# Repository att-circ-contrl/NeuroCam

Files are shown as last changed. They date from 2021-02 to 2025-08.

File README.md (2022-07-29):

# NeuroCam Experiment Monitoring System

## Overview

The NeuroCam is a set of scripts designed to aggregate video footage from
multiple cameras and to let a user monitor and annotate that footage in
real-time. Frame alignment is performed in post-processing, and video footage
is saved frame-by-frame to allow later analysis without motion-compression
artifacts.

**While this code is functional, there is a lot of room for improvement.**
This is documented in more detail in the "Idiosyncracies" section of this
document and in the "TODO" documentation in the code folder. Most of these
improvements will eventually happen, but refactoring NeuroCam is not
presently the lab's top priority.

The NeuroCam project is copyright (c) by Vanderbilt University, and is
released under the Creative Commons Attribution-ShareAlike 4.0 International
License.

## Quick-Start

The top-level Makefile automates common operations (under Ubuntu-derived
Linux, at least):

* Type "`make`" without arguments for the Makefile target list.

* To make a NeuroCam software install/update USB stick, put a USB stick in
your machine and type "`make installkey`".

* To rebuild the manuals (which should already be in the "`manuals`" folder),
type "`make manual`".

* To flash a "Blink Box" GPIO device using the firmware hex file, plug the
device into your computer and type "`make blinkbox-burn`".

* To rebuild the firmware for the "Blink Box" GPIO device, make sure
the "NeurAVR" project is installed and "`neuravr`" is symlinked at an
appropriate location (in the "`gpio/code`" folder or in the folder the
"`NeuroCam`" project is installed in), and type "`make blinkbox-hex`".

## Relevant Components

The following hardware and software components are provided:

* **Control daemon script.** This listens for commands on a UDP port, starts
and stops the camera daemon and GPIO daemon, and performs post-processing
tasks as requested.

* **Web interface script.** This is an old-school CGI script that provides a
GUI for configuring, controlling, and monitoring the output of the NeuroCam
control daemon.

* **Command-line interface program.** This is a command-line script that
can configure and command the NeuroCam control daemon.

* **"Blink Box" GPIO device.** This is a general-purpose TTL I/O box built
using Arduino hardware. The NeuroCam uses it to strobe LEDs for frame
synchronization and to listen for TTL signals (start/stop strobes and
annotation signals).

* **GPIO monitoring daemon.** This probes for "Blink Box" GPIO devices, and
if found, sets up LED strobing and translates GPIO inputs into appropriate
UDP commands that are sent to the NeuroCam control daemon.

The following helper scripts are provided:

* **Install and update scripts.** These are used to create NeuroCam software
installation USB sticks, which are then used to make new NeuroCams and to
update their software.

* **Utility scripts.** At present, this is a pair of scripts for sending UDP
packets and listening for UDP broadcasts. These are used for low-level
communication with the NeuroCam daemon for debugging purposes.

## Idiosyncracies

The following idiosyncracies are present (per "there is a lot of room for
improvement" in the overview section):

* Frame-grabbing has low jitter once it's been started but the individual
streams have time skew of up to 0.25 seconds relative to each other. This
is probably due to startup time of the frame-grabbing tool used (invoked via
shell call).

The workaround is to use LED strobing for frame alignment in post-processing.

* Compositing for monitoring and during post-processing takes far longer
than it should. This is probably due to using the Perl ImageMagick libraries
rather than writing a C utility using libjpeg to do it.

The workaround is to throw hardware at the problem (at least one core per
camera).

* Between capture time skew and compositing delay, there's about half a
second of time lag on the monitoring stream that the user sees. The frame
rate of the monitoring stream is also lower than the actual capture frame
rate (as the compositing process will drop frames as-needed; the frames
themselves are still saved).

The workaround is to click on a given individual feed in the web GUI to
select a specific raw feed, which is then forwarded without compositing,
if faster access is needed.

* The NeuroCam does not have a proper job manager (i.e. it isn't possible
to queue multiple operations). This is high on the list of features to
implement, but NeuroCam development is not presently the lab's top priority.

The workaround is to babysit the NeuroCam during post-processing and file
transfer. Folders (capture sessions) have to be processed, moved, or
deleted individually.

* The NeuroCam generates an absurdly large number of files (one per frame
per camera), and stores each camera's frames in a single directory.

This is intentional, but _many_ filesystems really hate having directories
with large numbers of files in them. In particular, the `exfat` filesystem
used on most external drives slows to a crawl, and the default Windows and
MacOS filesystems don't like it either. The default Linux filesystems
(`ext2`/`ext3`/`ext4`) are okay with it.

The workaround is to store NeuroCam folders as `.tar` archives when saving
them on external drives, and to process the frame data on Linux machines or
on other machines with suitable filesystems configured.

* The NeuroCam performs random access to an absurdly large number of files
during capture and post-processing.

This is intentional, and is unavoidable for data saved as individual frames.
It means that solid-state drives should be used when building NeuroCam
systems, as the seek time of magnetic drives would slow processing to a
crawl (and probably capture, too).

## Folders

This repository contains the following directories:

* `code` -- NeuroCam daemon and GUI scripts.
* `drawings` - Mechanical drawings (for the GPIO device).
* `gpio` -- Firmware source and PCB development files for the "Blink Box"
GPIO device.
* `hexfiles` -- Firmware binaries for the "Blink Box" GPIO device.
* `install-scripts` -- Scripts for building install/update USB sticks.
* `manuals` -- NeuroCam documentation.
* `manuals-src` -- Source for rebuilding NeuroCam documentation.
* `matlab` -- Matlab libraries for working with NeuroCam systems and data.
* `notes` -- Miscellaneous notes relevant to NeuroCam development.
* `schematics` - Schematics (for the GPIO device and lamp driver).
* `utils` -- Miscellaneous utility scripts for debugging the NeuroCam.

_This is the end of the file._

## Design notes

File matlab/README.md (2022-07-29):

# NeuroCam Experiment Monitoring System - Matlab Libraries

## Overview

This is a set of Matlab libraries and test scripts written to support the
use of the NeuroCam system.

These files are part of the NeuroCam project.
This project is Copyright (c) 2021 by Vanderbilt University, and is released
under the Creative Commons Attribution-ShareAlike 4.0 International License.

## Libraries

* `lib-ncam-video` --
Library for reading video frame information from a repository and for
extracting information about rapid brightness changes, to use for time
alignment.

## Sample Code

Sample code scripts are intended to illustrate how the libraries are used.
These also include my development test scripts. The following scripts are
provided:

* `do_align.m` --
Performs video frame alignment on a dataset using brightness changes in the
images (rather than LED blinks). This is intended to catch situations where
a computer monitor in view changes its depicted scene (a large change in
brightness in a one-frame time step). This should catch LED blinks too.

_This is the end of the file._

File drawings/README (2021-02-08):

EPS can be converted to DXF by loading into and saving from Inkscape.
This messes with the scale factor. I think it did 1 pt = 1 mm.

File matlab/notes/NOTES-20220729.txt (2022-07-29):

This is an interim partial version of the alignment script that makes
histograms of difference data but doesn't do anything else with it.

As far as I can tell by eye, the best way to proceed is to look for the most
variable sqrt(n) tiles in any given stream and average those, rather than
looking at the full-frame average.

It may also be a good idea to get a correlation matrix between tiles and
group tile sets that are most correlated, within a stream. This would catch
the case where two areas of the image are highly variable but are behaving
very differently.

Alternatively we could just select the top sqrt(n) tiles individually without
averaging them, and use each of them as alignment candidates against other
streams' tiles.

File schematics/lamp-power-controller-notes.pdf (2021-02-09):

Christopher Thomas <christopher.thomas.webmail@gmail.com>

## Lamp control circuit

2 messages

Christopher Thomas <christopher.thomas.webmail@gmail.com> | Wed, Nov 27, 2019 at 11:46 AM
To: "Haniff, Isaac J" <isaac.j.haniff@vanderbilt.edu>

Here are cleaned-up schematics and layout drawings for the lamp control circuit. It'll work as a general purpose "let a TTL line control a power supply" widget, so I figured you might eventually find it useful elsewhere.

My rating limits (24V 0.8A) are conservative. The actual limits are probably about 30V and 1.5A. The parts' absolute limits are 40V and 2A, but going anywhere near those is a bad and fire-prone idea.

The FETs are BS170 TO-92 ones (very common). The resistors should be at least 10k but other than that can be anything. The tiny 1" breadboard I used is Digikey part number 1568-1652-ND or SparkFun part number PRT-08808. The tiny box I used is Digikey part number HM-375-ND. The BNC pigtail was Digikey part number 314-1190-ND (handy to stock for many projects, but pricy). If you're screwing the board down rather than leaving it free-hanging, you'll want a 1/8" #4 stand-off, a #4-40 screw (1/2" or 5/8"), and a #4-40 hex nut as well.

I hope that you find this useful!

Regards,
-Christopher Thomas

### 2 attachments

lamp-control-schem.png
36K

lamp-control-bread-layout.png 133K

Christopher Thomas <christopher.thomas.webmail@gmail.com> | Wed, Nov 27, 2019 at 11:59 AM
To: "Haniff, Isaac J" <isaac.j.haniff@vanderbilt.edu>

In case you're wondering about some of the resistors: The BS170's maximum gate voltage is 20V. The resistors divide down the pull-up voltage, to tolerate a maximum of 40V. If you made the top resistors 20k and kept the others at 10k, you could tolerate up to 60V in, which is the same as the BS170's maximum drain-to-source voltage. This would only be a good idea if you knew the supply voltage was going to be high, though, as you want the gate voltage to be about 10V or higher to get decent current output.

For power calculations, the worst-case output resistance per transistor is 5 ohms, and absolute maximum power is 0.8W. That gives an absolute maximum current of 0.4A per transistor (at the worst-case resistance). If you've ever touched a 1W resistor with bare fingers, you'll understand why I added headroom. Junction-to-ambient thermal resistance is 150 degC/W, giving a 30 degC rise at my de-rated value (or 120 degC at their maximum; water boils at 100 degC).

Long story short, you can scale up output current by adding more FETs in parallel. FETS, unlike bipolars, have a negative temperature coefficient and so don't suffer from current hogging or thermal runaway. For much larger than this, you'd probably instead use a TO-220 FET bolted to a heat sink as the output driver.

Regards,
-Christopher Thomas
Gmail - Lamp control circuit | https://mail.google.com/mail/u/0?ik=50e6ba25c9...
1 of 1 | 2019-11-27, 12:01 p.m.

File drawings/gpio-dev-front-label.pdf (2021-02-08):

7 0

## Gnd GPIO TTL

Visible LEDs IR LED

7 0

## Gnd GPIO TTL

7 0

## Gnd GPIO TTL

Visible LEDs IR LED

7 0

Gnd

Visible LEDs

## GPIO TTL

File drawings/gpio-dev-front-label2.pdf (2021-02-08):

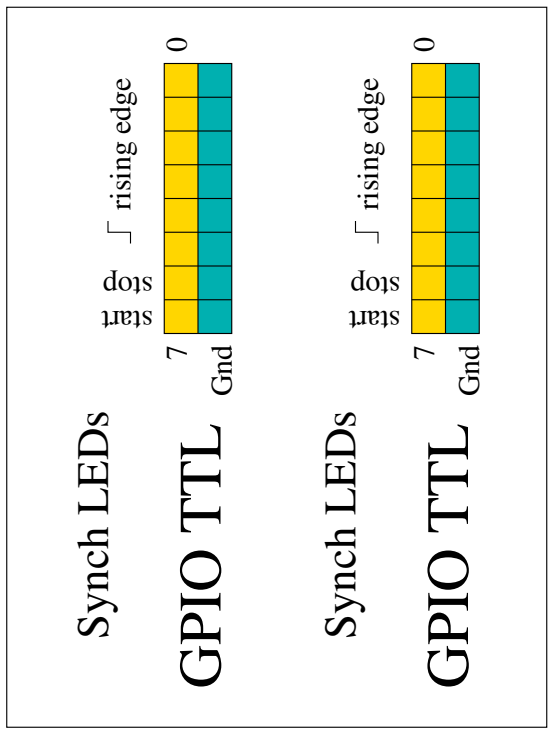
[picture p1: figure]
Gnd GPIO TTL; Synch LEDs

Gnd GPIO TTL; Synch LEDs

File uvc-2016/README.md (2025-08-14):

# UVC Driver Notes

The 2016 version of the NeuroCam (running on Mint 17) had an issue where
certain cameras would attempt to grab all of the available USB bandwidth.
This folder contains the diff made to "`uvc_video.c`" to address that issue,
along with additional notes.

For further details, see `notes/NOTES-uvc`.

Systems based on later versions of Mint did not appear to have this issue.

_This is the end of the file._

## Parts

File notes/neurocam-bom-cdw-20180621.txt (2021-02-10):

Machine (no RAM):  NUC6i7KYK  CDW p/n: 4085713   (545.99 USD)
RAM:  Kingston DDR4 2x4gig  CDW p/n: 4039935   (114.99 USD)
SSD:  (1 TB) Samsung MZ-N5E1T0BW  CDW p/n: 4150865   (418.99 USD)
(3x) Camera:  Logitech C920  CDW p/n: 2588857   (72.99 USD)
USB hub:  StarTech 4-port  CDW p/n: 3069185   (25.99 USD)
Router:  Asus N16  CDW p/n: 1953395  (93.99 USD)
[alternate: Asus RT-N66R  CDW p/n:  4493141  (93.99 USD)]
Patch cable:  Tripp Lite 3' Cat5e  CDW p/n: 324473  (2.99 USD)

Unit cost:  1422 USD (approx)

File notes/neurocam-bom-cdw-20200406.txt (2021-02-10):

Part			mfg p/n		cdw p/n		price

machine (no RAM)	NUC7i7DNKE	5008529		659.99
https://www.cdw.com/product/intel-next-unit-of-computing-kit-nuc7i7dnke-mini-pc-core-i7-8650u-1.9-g/5008529

RAM (1x8 gigs)		KCP426SS8/8	5109912		43.99
https://www.cdw.com/product/kingston-ddr4-8-gb-so-dimm-260-pin-unbuffered/5109912

SSD (1 TB)		MZ-N6E1T0BW	4934196		183.99
https://www.cdw.com/product/samsung-860-evo-mz-n6e1t0bw-solid-state-drive-1-tb-sata-6gb-s/4934196

Router			RT-N66R		4493141		99.99
https://www.cdw.com/product/asus-rt-n66r-wireless-router-802.11a-b-g-n-desktop/4493141

USB hub (usb 3)		ST4300MINU3B	3069185		25.99
https://www.cdw.com/product/startech.com-portable-4-port-superspeed-mini-usb-3.0-hub-black/3069185

Network cable (3')	N001-003-BL	324473		2.99
https://www.cdw.com/product/tripp-lite-3ft-cat5e-cat5-350mhz-blue-snagless-molded-patch-cable-rj45-m-m/324473

Total:							1016.94

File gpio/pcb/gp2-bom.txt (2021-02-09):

Gp2 Uno shield rc1 bill of materials (USD):

Item                    Digikey p/n        Unit Price    Qty      Cost

header male 1x6         732-5319-ND         0.33          1        0.33
header male 1x8         732-5321-ND         0.37          2        0.74
header male 1x10        732-2670-ND         0.89          1        0.89
header female 2x3       S7071-ND            0.61          1        0.61
header male 2x6 shr     SAM12292-ND         2.80          1        2.80
header male 2x8 shr     S9171-ND            0.42          1        0.42

resistor 0805 680 ohm   P680CCT-ND          0.11          1        0.11
resistor 0805 47 kohm   P47.0KCCT-ND        0.11          1        0.11
resistor 0805 475 kohm  P475KCCT-ND         0.10         12        1.20

Subtotal:                                                          7.21

Gp2 faceplate rc3 bill of materials (USD):

Item                    Digikey p/n        Unit Price    Qty      Cost

header male 2x6 shr     SAM12292-ND         2.80          1        2.80
header male 2x8 shr     S9171-ND            0.42          1        0.42

BNC jack (pcb) 50 ohm   WM5278-ND           4.03          8       32.24
LED green 3mm           4303F5-ND           0.61          1        0.61
LED red 3mm             4303F1-ND           0.59          1        0.59
switch pb SPST          SW1021CT-ND         1.00          1        1.00

transistor nfet to-92   BS170-ND            0.56          8        4.48

resistor 0805 680 ohm   P680CCT-ND          0.11          8        0.88
resistor 0805 47 kohm   P47.0KCCT-ND        0.11          1        0.11

Subtotal:                                                         43.13

Auxiliary hardware (USD):

Item                    Digikey p/n        Unit Price    Qty      Cost

Arduino Uno rev3        1050-1024-ND       23.38          1       23.38

(no such thing as a 12-position pre-assembled cable.)
ribbon cable 12pos 1m   732-11802-ND        2.55          1        2.55
IDC connector 12pos     A113153-ND          1.88          2        3.76

box metal/abs 6.3"x6.5" HM904-ND           21.45          1       21.45

USB B panel mount       1528-1570-ND        3.95          1        3.95
USB A-B cable 3'        1175-1087-ND        2.48          1        2.48

spacer nylon 4-40 3/4"  36-1902D-ND         0.90          4        3.60
spacer nylon #4 1/16"   492-1071-ND         0.0520        6        0.31
screw nylon 4-40 3/4"   H550-ND             0.0926        4        0.37
screw nylon 4-40 1/4"   H542-ND             0.0886        4        0.35
screw metal 4-40 3/8"   HM1456-ND           0.109         6        0.65
hex nut nylon 4-40      36-9605-ND          0.161        10        1.61

Subtotal:                                                         64.46

Printed circuit boards (USD):
(via Seeed Studio, in quantity 10)

Item                                       Unit Price    Qty      Cost

front panel PCB                             1.832         1        1.83
shield PCB                                  0.49          1        0.49

Subtotal:                                                          2.32

Grand total:                                                     117.12

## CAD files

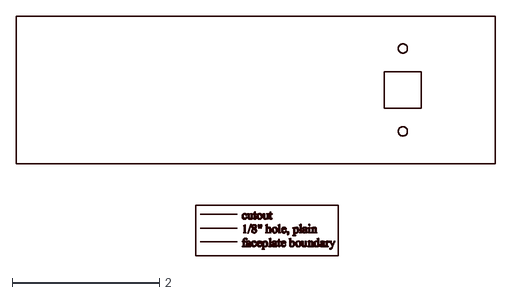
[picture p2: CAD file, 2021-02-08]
drawings/gpio-v2-back-inches.dxf
6.50 x 3.25

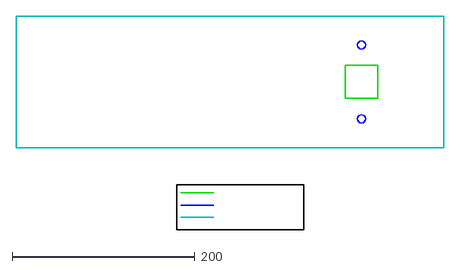
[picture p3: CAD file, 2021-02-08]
drawings/gpio-v2-back.dxf
468.0 x 234.0

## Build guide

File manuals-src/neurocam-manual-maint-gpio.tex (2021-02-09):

% NeuroCam manual - GPIO/Synch Boxes
% Written by Christopher Thomas.
% Copyright (c) 2021 by Vanderbilt University. This work is released under
% the Creative Commons Attribution-ShareAlike 4.0 International License.

\chapter{GPIO and Synch Box}
\label{gpio}

The GPIO-and-synch box provides TTL-level inputs via a rectangular connector
and TTL-level synchronization outputs via BNC connectors. Changes to inputs
are reported to the NeuroCam computer via USB cable.

During normal operation of the NeuroCam system, the following functions are
performed:
\begin{itemize}
\item The synchronization lines are strobed high for 20~ms every 10 seconds,
with changes in the outputs recorded in session log files.
\item Changes to TTL inputs are recorded in session log files.
\item Low-to-high transitions on input bits 7 and 6 cause the NeuroCam to
start and stop recording a session, respectively. There is a ``dead time''
of 10 seconds between successive commands being recognized.
\end{itemize}

The front panel and interior of a GPIO-and-synch box are shown below:

\begin{center}
% The exterior image is 800x600, the interior is 600x600.
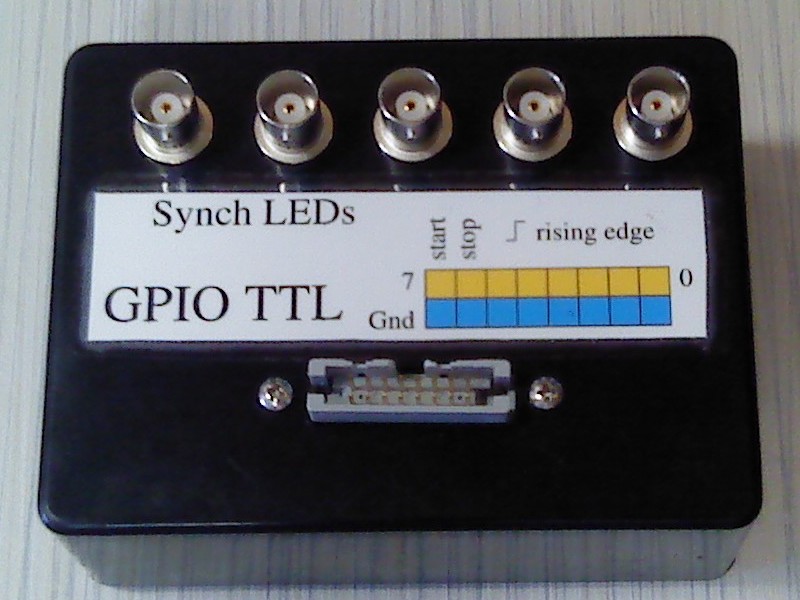
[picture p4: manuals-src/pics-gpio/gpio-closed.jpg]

\hspace{1in}
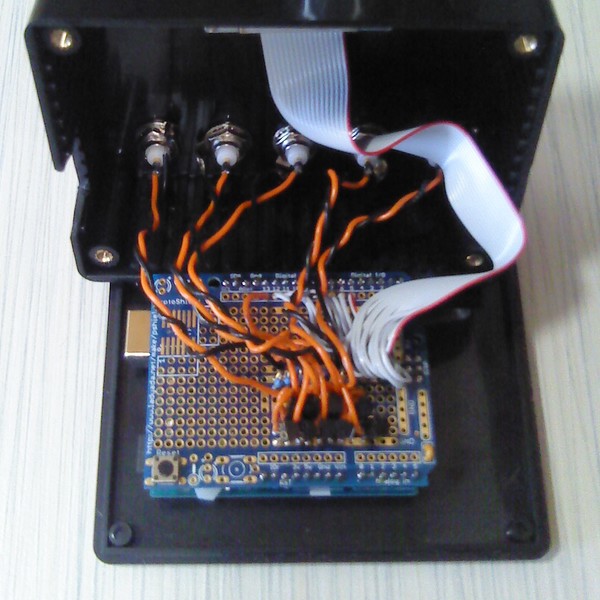
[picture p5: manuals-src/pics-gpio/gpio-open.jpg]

\end{center}

\clearpage
The parts needed for a GPIO-and-synch box are as follows:

\begin{tabular}{llll}\hline
Qty & Description & Manuf. p/n & Digikey p/n \\
\hline
%
1 & Arduino Uno rev3 & A000066 & 1050-1024-ND \\
1 & Arduino prototyping shield kit & 2077 & 1528-1207-ND \\
9 & NFET TO-92 & BS170 & BS170-ND \\
3 & resistor 4.75 kohm 0.25w & MFR-25FBF52-4K75 & 4.75KXBK-ND \\
7 & resistor 475 ohm 0.25w & MFR-25FBF52-475R & 475XBK-ND \\
5 & BNC jack panel mount & 31-221-RFX & ARFX1064-ND \\
1 & box abs 4.3x3.2x1.7 & 1591SBK & HM121-ND \\
1 & conn 16 pin female to ribbon & M1YXK-1636J & M1YXK-1636J-ND \\
2 & machine screw 4-40 0.5in ss & 9902 & 36-9902-ND \\
2 & hex nut 4-40 ss & 7248-3 & 36-7248-3-ND \\
4 & machine screw 4-40 0.375in nylon & 9528 & 36-9528-ND \\
4 & hex nut 4-40 nylon & 9605 & 36-9605-ND \\
1 & USB cable male A to male B & 102-1030-BE-00200 & 1175-1089-ND \\
%
\hline
\end{tabular}

\textbf{NOTE:} The prototyping shield kit includes male pin headers,
one female ISP header, two decoupling capacitors, one pushbutton switch,
one red LED, and one green LED, which are required for the GPIO-and-synch
box.

The prototyping shield kit should be assembled per its directions. There are
several important things to keep in mind:
\begin{itemize}
%
\item The pin headers (including ISP header) should be plugged into an
Arduino Uno, with the prototyping shield board friction-seated on the header
pins, prior to soldering. This guarantees proper mechanical alignment of the
headers.
%
Do not use the long-tail female ``stacking'' headers for I/O pins. These
do not mate properly with the Arduino Uno. The only female header used is
for the ISP header connection.
%
\item The two decoupling capacitors should be soldered in their marked
positions on the board.
%
\item Only one of the two provided switches is used. This is soldered to
the ``reset switch'' location indicated on the board.
%
\item The red and green 3mm LEDs are not soldered to the prototyping board.
They are used for strobe and power lights on the front panel of the
GPIO-and-synch box if such lights are desired. They mount in 1/8" holes,
and should be secured in place using epoxy on their rear sides.
%
\end{itemize}

\clearpage
The following circuit should be built on the prototyping shield:

\begin{center}

\end{center}

A mechanical drawing of the front panel is as follows:

\begin{center}

\end{center}

The rear panel should have mounting holes compatible with the Arduino Uno
(1/8", countersunk).

%
% This is the end of the file.

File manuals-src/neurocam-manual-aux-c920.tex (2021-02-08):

% NeuroCam manual - IR modifications for Logitech c920.
% Written by Christopher Thomas.
% Copyright (c) 2021 by Vanderbilt University. This work is released under
% the Creative Commons Attribution-ShareAlike 4.0 International License.

\chapter{IR Modifications for Logitech C920 Camera}
\label{c920}

The Logitech C920 webcam can be readily modified for near-infrared use. This
involves the following actions:
\begin{itemize}
\item Disassembling the camera.
\item Removing the optics assembly from the board.
\item Removing the infrared filter from the optics assembly.
\item Replacing the infrared filter with glass plates of appropriate
thickness.
\end{itemize}

Detailed documentation of these actions is described below.

\section{Confirm Camera Identity}

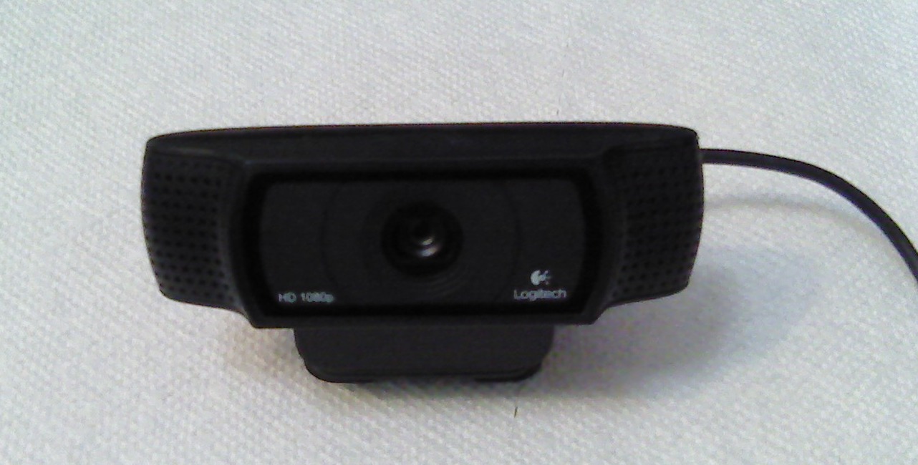
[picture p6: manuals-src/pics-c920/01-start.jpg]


This documentation only applies to the Logitech C920 camera. Other cameras,
even closely-related models, have different internal layouts and methods of
disassembly.

\section{Remove Stickers and Microphone Guards}

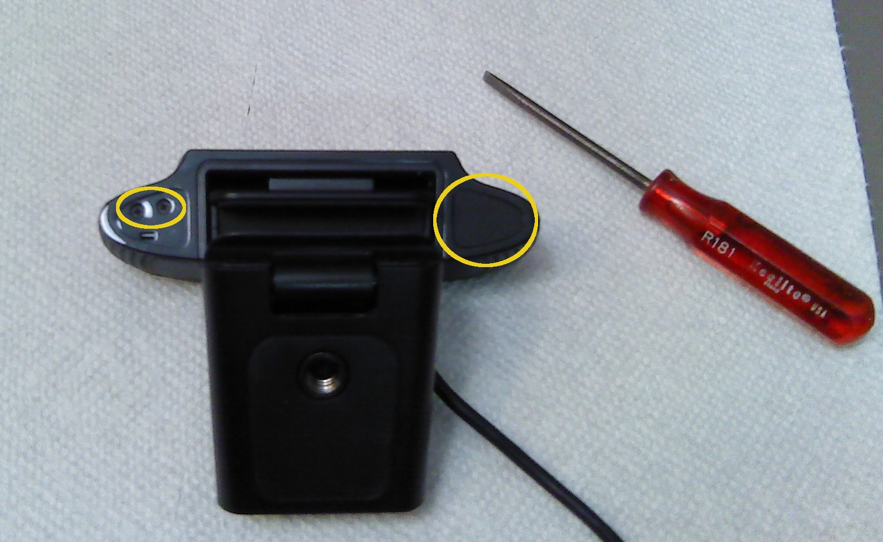
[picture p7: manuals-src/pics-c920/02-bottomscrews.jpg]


The screws securing the microphone guards are covered by two layers of
stickers. Both layers must be removed to access them.

\section{Remove Cover}

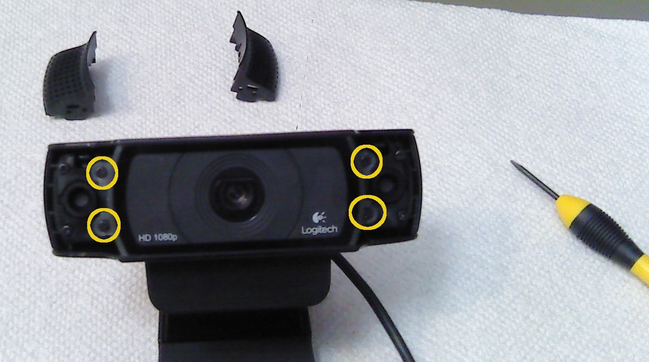
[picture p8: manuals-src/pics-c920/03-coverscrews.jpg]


\section{Remove Mounting Bracket}

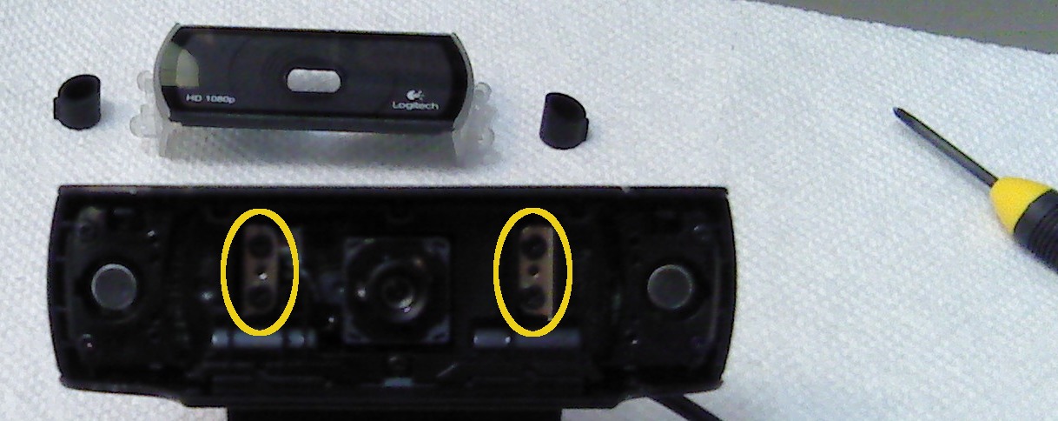
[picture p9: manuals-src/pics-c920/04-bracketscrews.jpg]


There is a peg between each pair of bracket screws. To remove the mounting
bracket, rotate the bracket so that its metal flanges lift off of these pegs.
The flanges will then slide out of the camera easily.

\section{Remove Spacer}

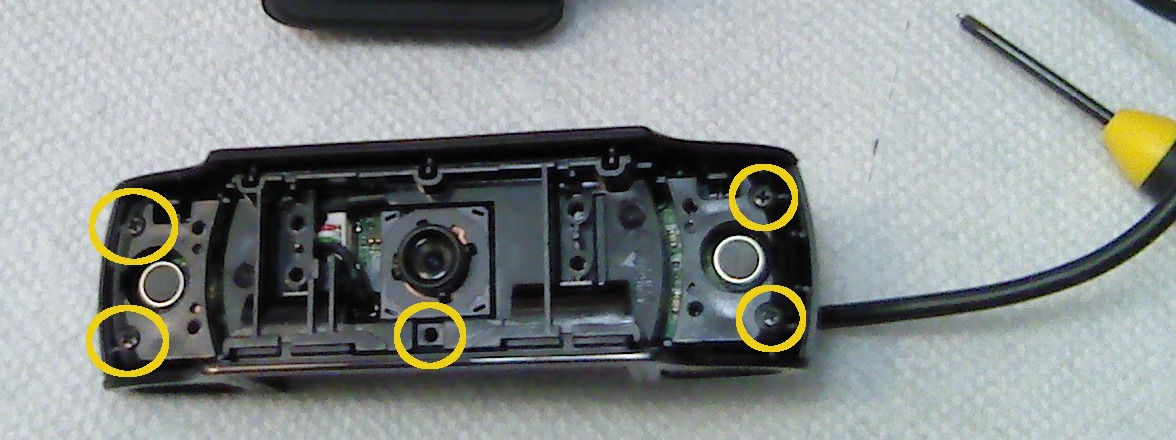
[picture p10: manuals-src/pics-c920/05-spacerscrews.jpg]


\section{Remove Board}

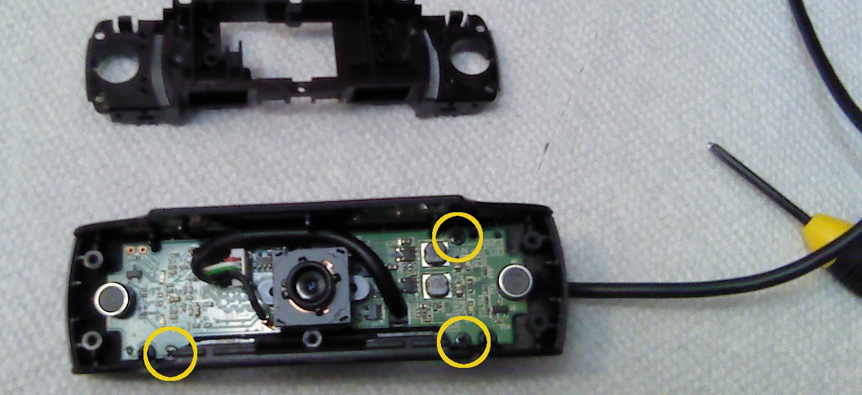
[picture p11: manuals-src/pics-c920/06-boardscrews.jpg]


The USB cable is fixed to the case. The board can be removed by rotating it,
while bending the side of the case slightly to release the catches that secure
the board and the USB cable. Do not bend the board itself (that may destroy
it).

Alternatively, the USB cable can be unplugged from the board (via the header
and ground pin). This is risky, as both connectors are easy to damage.

\section{Optional: Remove LEDs}

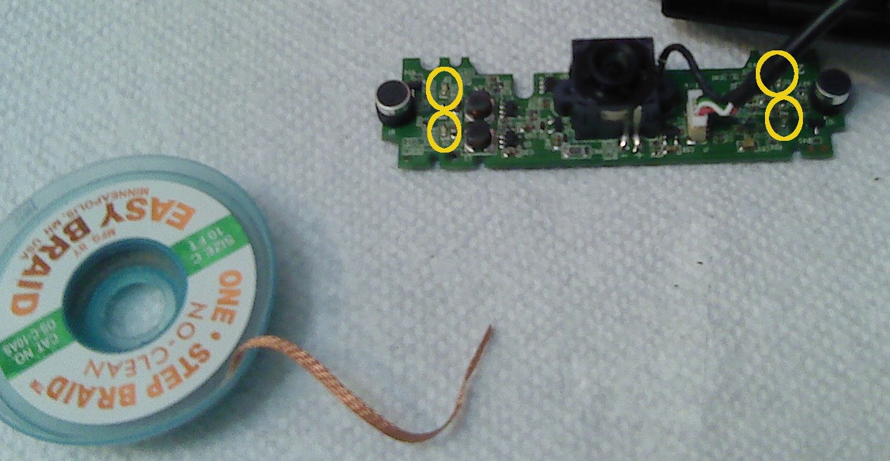
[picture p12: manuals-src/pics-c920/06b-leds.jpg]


The camera status LEDs are white rectangular components with labels ``D3''
through ``D8''. Only four of the six positions are populated. These can be
removed using ``solder wick'' per Step \ref{sect-920-desolder} if desired.
Tearing pads is tolerable, as long as no other traces or components are
disturbed.

Do not use a heat gun. Hot air will desolder other nearby components and may
blow them out of position.

\section{Unscrew Optics Assembly}

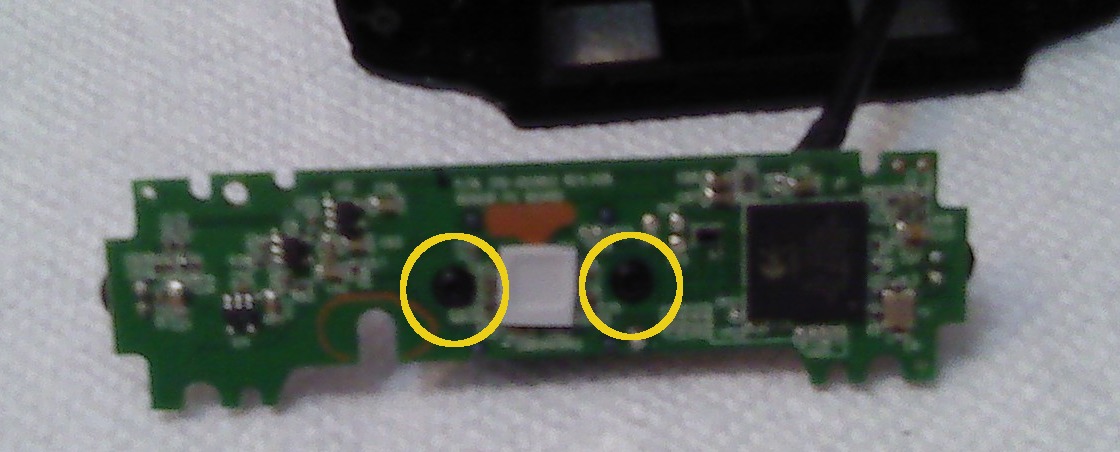
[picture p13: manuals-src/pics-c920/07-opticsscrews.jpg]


After being unscrewed, the optics assembly will remain secured to the board
by its soldered contacts.

\section{Un-Solder and Remove Optics Assembly}
\label{sect-920-desolder}

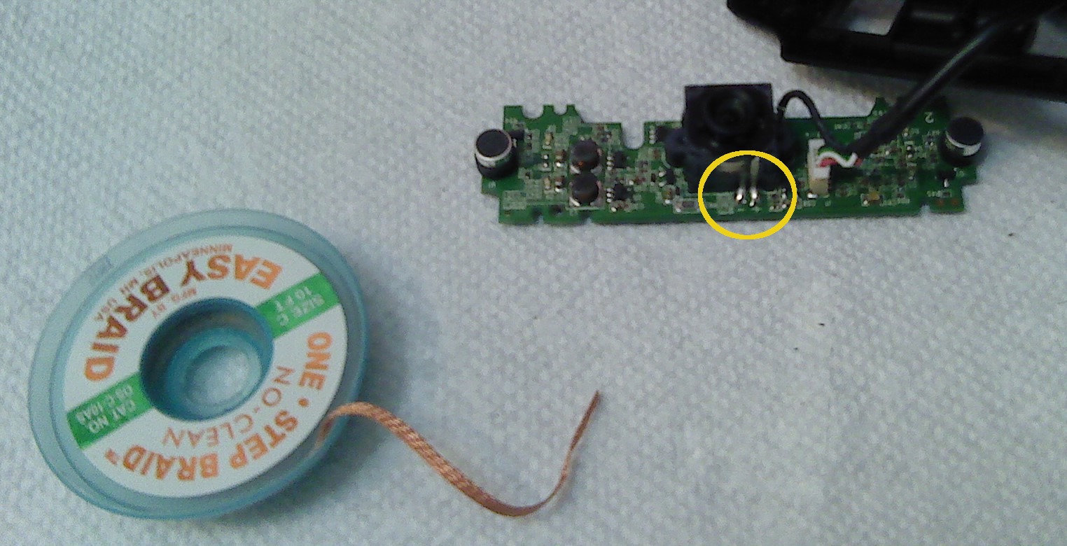
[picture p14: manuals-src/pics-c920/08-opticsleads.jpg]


The optics assembly leads can be desoldered using ``solder wick'' (also
called ``desoldering braid''). A variety that has flux in the braid is
recommended (though flux can be applied separately if necessary). Setting
the iron to high temperature makes desoldering easier, but care must be
taken to avoid heat damage to nearby components.

Be gentle when removing the optics assembly, as the contact pads it's
soldered to can be torn off of the board if they're still partly bonded to
the leads.

Do not use a heat gun. The sensor die is nearby and may be damaged. The
anisotropic film holding the sensor die to the board may also be damaged.

\section{Verify Absence of Damage and Dust}

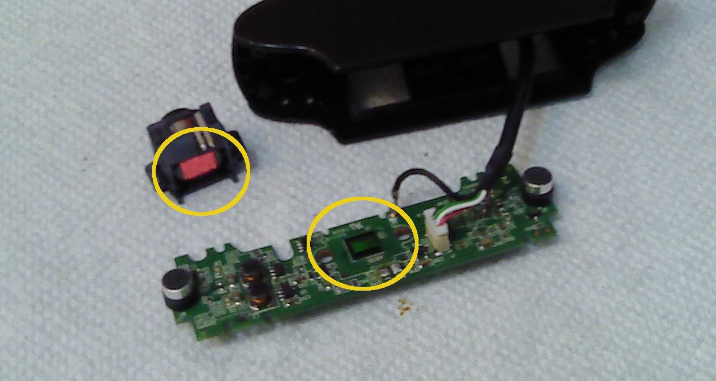
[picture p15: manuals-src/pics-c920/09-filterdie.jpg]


The IR filter (in the optics assembly) and sensor die (on the board) are now
visible.

The sensor die is fragile (and has a fragile coating). It should be visually
inspected to confirm that no scratches or dust particles are present. Take
care not to breathe on it while inspecting it, as moisture will leave droplets
on the die.

If moisture or dust are present on the die, the die can be cleaned by wiping
it very gently using ``lens tissue'' (also called ``lens paper''). Wiping that
is not sufficiently gentle will instead scratch the die by dragging dust
particles across it.

The lens tissue may be soaked in alcohol prior to wiping. This makes it
easier to safely remove dust, and is the only way to remove water stains,
but it is possible that alcohol may damage the coatings on the die. Wipe
diagonally from one corner of the die to the other, to minimize the amount
of liquid that clings to the trailing edge of the die, and then wipe again
with a dry piece of lens tissue (or a dry corner of the same piece).

Do not allow alcohol to contact the anisotropic film holding the die to the
board, as it will likely cause delamination.

\section{Heat Infrared Filter}

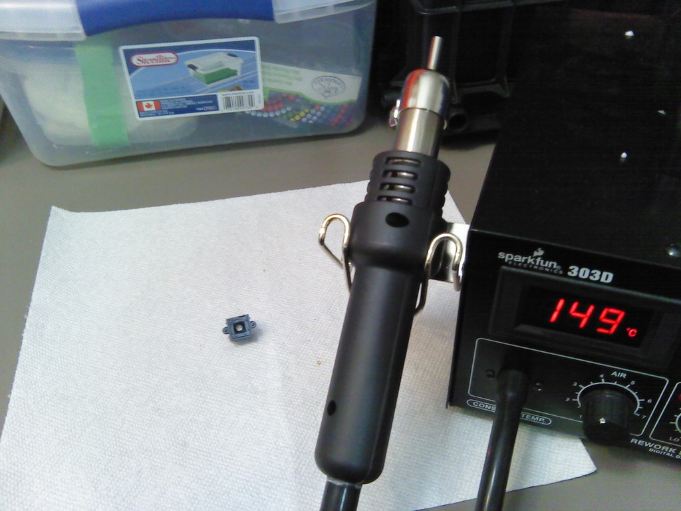
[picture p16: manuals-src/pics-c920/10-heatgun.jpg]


The infrared filter plate is bonded to the optics assembly with glue. Play a
heat gun around the edge of the filter plate to soften this glue. Use a
circular motion to avoid overheating any one part of the edge or allowing any
other part to cool. Use a low temperature setting to avoid cracking the plate
due to heat shock and to avoid melting the plastic housing.

\section{Remove Infrared Filter}

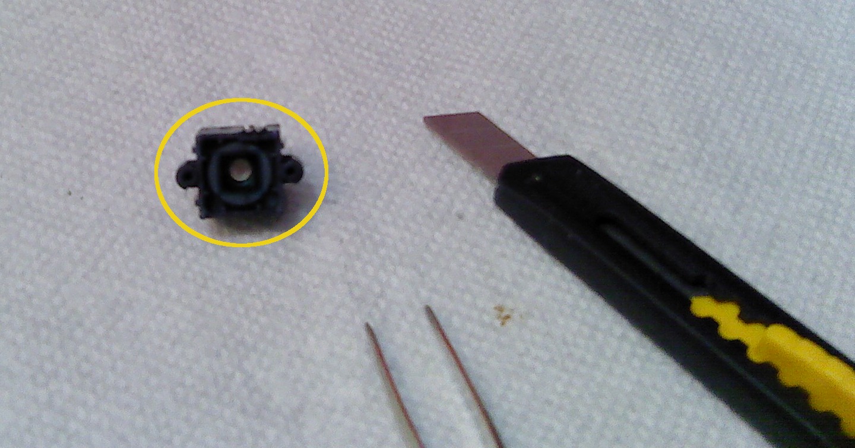
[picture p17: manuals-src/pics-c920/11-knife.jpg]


Use the edge of a sharp knife to pry the filter plate out of the optics
assembly. Lift from one corner, letting the plate hinge on one of the
opposing edges. If there is any resistance, use the heat gun again to soften
the glue.

Discard the filter plate after removal.

\section{Scribe Microscope Cover Slips}

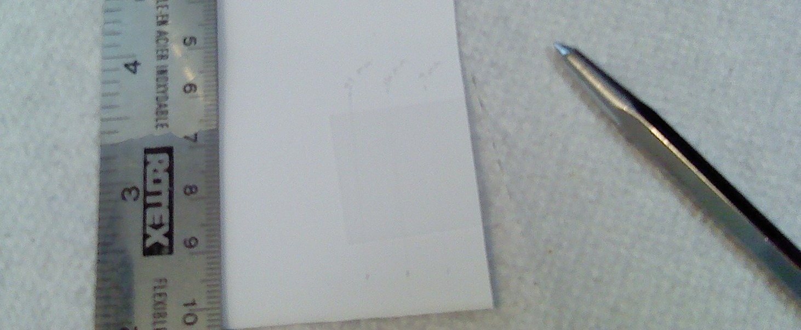
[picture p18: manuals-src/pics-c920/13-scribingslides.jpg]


The filter plate is 7mm by 7mm by 0.31mm. It must be replaced by one or more
pieces of glass with a total thickness of 0.35mm or more for the camera to
focus properly. This corresponds to the thickness of two \#2 microscope cover
slips (also called ``cover glasses'').

To cut these cover slips, draw guide lines on to a sheet of paper, line
up the edge of the cover slip with one guide line, place a straightedge
over the other guide line, and scribe the glass several times using a
carbide-tipped scribing tool. Carefully snap the cover slip along this line
(holding it with the scribed side facing away from you, and then bending it
so that it bows outwards in that direction).

\textbf{Take extreme care to clean up flakes and slivers of glass.} These
will be produced, and are incredibly sharp (their edges are as thin as a
single atom).

Cut the cover slip sections slightly smaller than 7mm by 7mm; there is no way
to trim them after they are cut.

\section{Wash Cover Slip Plates}

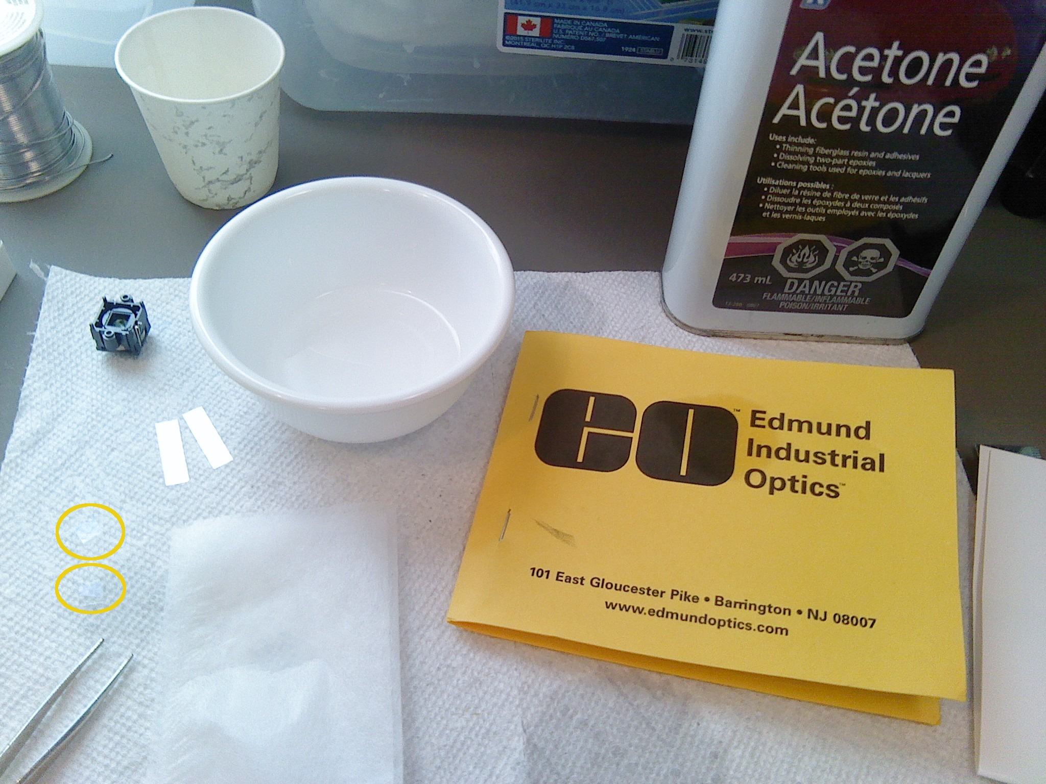
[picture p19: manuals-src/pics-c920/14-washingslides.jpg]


The cover slip plates must be absolutely free of dust and of oils before
being bonded to the optics assembly. To ensure this, pour acetone into a
small glass or ceramic dish, grasp the edges of a plate with tweezers,
submerge the plate in acetone, and agitate it for a few seconds. Place the
plate onto a dry piece of lens tissue, fold the paper over, and wipe the
plate to remove droplets of acetone and remaining dust. Set clean plates
aside on another piece of lens tissue.

Take care to grasp the plates by the edges, with tweezers. Grasping the
faces will scrape the surfaces of the plates. Squeezing too hard at the
edges will shatter the plates. Grasping faces with fingers will deposit
grease on the plates, and grasping edges with fingers will result in
injury, as snapped edges have atom-thin sharp cusps.

\section{Glue Cover Slip Plates into Optics Assembly}

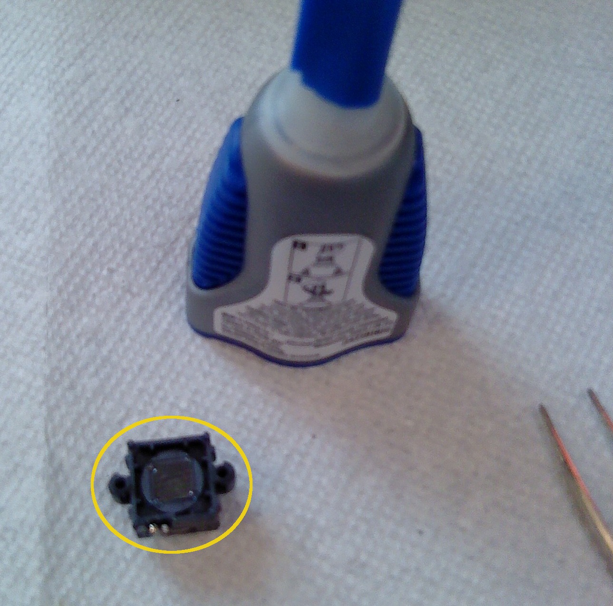
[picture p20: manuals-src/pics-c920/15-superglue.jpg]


Carefully stack two cover slip plates into the frame that was occupied by
the IR filter. Carefully apply a bead of cyanoacrylate glue (``super glue'')
to each corner of the frame, wiping the bead outwards (away from the middle
of the plate) when applying it. Wipe each bead again with a piece of lens
tissue to reduce the bead's height.

Do not bond the edges of the frame; just the corners. There has to be ample
space for cyanoacrylate vapours to escape to avoid frosting the plates or
the optics within the assembly. Use a new piece of lens tissue every time
you wipe a bead of glue, to avoid smearing glue on to the cover slip plates.
Be very gentle when applying or wiping glue, to avoid popping the cover slip
plates out of the frame. Cover slip plates can be re-seated using tweezers
if this occurs.

Allow the glue to dry for at least 5 minutes before mounting the optics
assembly back on to the camera board.

%
% This is the end of the file.

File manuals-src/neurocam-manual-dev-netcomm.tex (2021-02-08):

% NeuroCam manual - Network Communication Between Components
% Written by Christopher Thomas.
% Copyright (c) 2021 by Vanderbilt University. This work is released under
% the Creative Commons Attribution-ShareAlike 4.0 International License.

\chapter{Network Communication Between Components}
\label{netcomm}

\section{Overview}

The NeuroCam software consists of several components that interact via UDP 
network messages. A diagram is shown below:



The camera daemon collects local camera video and collects video frames and 
UDP messages from external sources (using the handshaking protocol 
described in Chapter \ref{handshake}).
The GPIO daemon monitors USB-attached serial tty devices, talks to ones
that recognize its handshaking protocol, and reports changes to their state.
The manager daemon coordinates activities at the top level, and a web CGI 
script processes user requests and turns these into commands that are sent 
to the manager daemon.

This architecture was chosen for modularity/compartmentalization. In 
particular, the CGI web interface may be replaced with any other interface
that can talk to the manager daemon over UDP.

% FIXME - Force a page break.
\clearpage
The ports reserved for these communications are defined in the
``\verb+network+'' library file. A summary is below:

\begin{tabular}{ccp{0.7\columnwidth}} \hline
Port & Used By & Purpose \\ \hline
%
7xxx & other &
Default port address range for the network library. Chosen to not conflict
with any other port ranges. \\
\hline
8080 & \verb+fakeunity+ &
Port on which the fake game utility offers its video feed. \\
8090 & (camera) \verb+daemon+ &
Port on which the camera daemon offers the monitoring video feed. \\
8888 & game, \verb+fakeunity+ &
Broadcasts asking for external information sources (videos, UDP messages)
are made to this port. Anything with information to offer should listen 
at this address. \\
\hline
9xxx & (camera) \verb+daemon+ &
Port range reserved for the camera daemon. \\
9998 & (camera) \verb+daemon+ &
Port on which the camera daemon tells itself that it's finished assembling 
a monitoring frame. \\
9999 & (camera) \verb+daemon+ &
Port on which the camera daemon listens for commands. \\
\hline
10xxx & \verb+manager+ &
Port range reserved for the manager daemon. \\
10999 & \verb+manager+ &
Port on which the manager daemon listens for commands/queries. \\
\hline
11xxx & \verb+fakeunity+ &
Port address range reserved for the fake game utility. This is chosen to not 
conflict with any other port ranges. This has to be set to something, because 
the network library can reserve access to ports when used and these will not 
be released until the fake game utility terminates. \\
\hline
12xxx & \verb+cgi+ web script &
Port address range reserved for the CGI script. \\
\hline
13xxx & \verb+mjpeg+ library &
Port range reserved for internal communication by the multithreaded version 
of the video serving function. Multiple instances of that function will 
use overlapping ranges and fight over ports, so the single-threaded version 
should be used when possible. \\
\hline
14000 & \verb+gpio+ &
Port on which the GPIO daemon listens for commands/queries. \\
%
\hline
\end{tabular}

\section{Manager Daemon}

The manager daemon is responsible for starting and stopping the camera daemon,
for ensuring that the GPIO daemon is running, and for performing 
post-processing and other repository manipulations.

The manager daemon listens for UDP packets on port 10999. Commands are
plain text strings.

Multiple commands may be issued in sequence (the manager will accept and
make note of new commands while processing previous commands). Some commands,
like status queries, will be executed immediately even if other tasks are
ongoing; others, like post-processing tasks, will be queued in sequence.

\textbf{NOTE:} Directory paths and filenames are \textbf{not checked}. A
malicious user could abuse this, so it is \textbf{strongly recommended} that 
all such names be script-generated and not based on user input.

Status query command:
\begin{itemize}
\item ``\verb+what is your status reply to port NNNN+''
\end{itemize}

% FIXME - Force a page break.
\clearpage
Status responses:
\begin{itemize}
\item ``\verb+idle+''
\item ``\verb+running cameras+''
%
\item ``\verb+busy (doing what) (progress string)+''

The progress string is optional, and is always in parentheses if present.
The operation specifier (also optional but usually present) is one of the
following:
\begin{itemize}
\item ``\verb+synchronizing timestamps+''
\item ``\verb+compositing+''
\item ``\verb+transcoding+''
\item ``\verb+archiving+''
\item ``\verb+calculating sizes+''
\item ``\verb+removing post-processed files+''
\item ``\verb+removing session folder+''
\item ``\verb+copying session folder+''
\item ``\verb+synchronizing disks+''
\item ``\verb+generating preview+''
\item ``\verb+auto-adjusting cameras+''
\end{itemize}
%
\end{itemize}

Diagnostics commands:
\begin{itemize}
\item ``\verb+debug version to port NNNN+''

The response to this is a version string.

\item ``\verb+debug report to port NNNN+''

The response to this is one or more messages describing the manager's internal
state and the last command processed.
\end{itemize}

Session commands:

\begin{itemize}
\item ``\verb+start cameras repository=(dir) config=(file)+''

Specifying ``\verb+auto+'' for the repository or config file tells the
manager to choose its own values for those parameters. An automatic
repository name will be based on a timestamp.

A copy of the configuration file will be placed in the new session folder.

\item ``\verb+stop cameras+''
\item ``\verb+shut down+''
\end{itemize}

% FIXME - Force a page break.
\clearpage
Monitoring commands (used only while recording):
\begin{itemize}
\item ``\verb+feed (subdir name)+''

The default feed is ``\verb+Monitor+'', which is a stitched-together tiling
of all video feeds. Other feed names just copy one stream's frames directly.
\end{itemize}

Video configuration commands (used only while not recording):
\begin{itemize}
\item ``\verb+snapshot config=(file) outdir=(dir)+''

This acquires frames from all local cameras and all non-local video streams,
saving the results in the ``\verb+auxfiles+'' directory.

\item
``\verb+autocamadjust config=(file) size=(resolution wanted) rate=(fps wanted)+''

This walks through all cameras, adjusting size and exposure settings until
the desired frame rate is obtained. First exposure time is reduced, and if
that fails to produce the desired frame rate size is reduced and the process
repeats. This is very time-consuming.
\end{itemize}

Post-processing commands (used only while not recording):
\begin{itemize}
\item ``\verb+timeshift repository=(dir)+''

This adjusts each video stream's timestamps so that LED flashes are 
synchronized. Only produces valid results if flashes are present.

This creates a modified log file (``\verb+logfile-timed.txt+'') with 
altered timestamps.

\item ``\verb+composite repository=(dir)+''

Assembles a ``Composite'' video feed. This stitches together frames from all
other video feeds, in the same manner as the ``Monitor'' feed, but does so at
higher resolution, with no dropped frames, and with a visible timestamp 
annotation.

This creates a modified log file (``\verb+logfile-composited.txt+'') with
frame events for the ``\verb+Composited+'' video feed inserted.

\item 
``\verb+transcode repository=(dir) stream=(subdir name) output=(file w/o suffix)+''

This assembles frames from one video feed directory into a playable compressed
video file (typically ``\verb+.mp4+'' format).

\textbf{NOTE:} because this performs lossy compression on what was already 
lossy-encoded MJPEG data, the image quality of frames suffers. Compressed 
video files are intended for user preview purposes, not automated processing.

\item ``\verb+archive rootdir=(dir) output=(file without suffix)+''

This creates a ``\verb+.tar+'' archive with the contents of a directory
(typically a session folder). This is intended to allow convenient web 
download of a folder's contents.

\item ``\verb+unprocess repository=(dir)+''

This removes all post-processing files associated with a directory (which
should be a session folder). This includes modified/annotated log files,
compressed video streams, the ``Composite'' video stream's folder, and any
``\verb+.tar+'' archive created of this directory.

\item ``\verb+cancel processing+''

This halts post-processing. The command in progress is killed, remaining
queued commands are purged, and an ``\verb+unprocess+'' command is
automatically queued for execution.
%
\end{itemize}

Repository manipulation commands (used only while not recording):
\begin{itemize}
\item ``\verb+metadata rootdir=(dir)+''

This refreshes metadata for all session folders within a given repository
root directory. This can take quite a while, as updating a changed session 
folder potentially involves checking metadata for millions of files.

\item ``\verb+copy source=(dir) dest=(dir)+''

This duplicates a directory tree (which is intended to be a session folder). 
The original is left intact; for a ``move'' operation, issue a 
``\verb+delete+'' command following this one.

\item ``\verb+delete repository=(dir)+''

This removes a directory tree (which is intended to be a session folder).

\item ``\verb+disksynch+''

This issues a ``\verb+sync+'' command, committing changes to disk. This is
intended to allow safe removal of USB drives, which can take substantial
amounts of time to commit changes.
%
\end{itemize}

\section{Camera Daemon}

\fixme{Content goes here.}

\section{GPIO Daemon}

\fixme{Content goes here.}

Talk about handshaking with GPIO devices over USB-serial.

\section{Web Interface Notes}

\fixme{Content goes here.}

Talk about where scratch files go, what the default directories are,
and the paradigm the CGI script uses.

\fixme{Stopped here.}

%
% This is the end of the file.

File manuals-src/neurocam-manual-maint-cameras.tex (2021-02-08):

% NeuroCam manual - Cameras
% Written by Christopher Thomas.
% Copyright (c) 2021 by Vanderbilt University. This work is released under
% the Creative Commons Attribution-ShareAlike 4.0 International License.

\chapter{Cameras}
\label{cameras}

\section*{Camera Selection}

The NeuroCam system is compatible with any UVC-compliant USB camera capable
of producing MJPEG output. That said, there are several additional qualities
that cameras \textit{should} possess:

\begin{itemize}
\item The camera should support 1280x720 or better resolution at 30~fps.
\item The camera should either not have an infrared filter or should have an
infrared filter than can be easily removed (not bonded to the sensor die).
\item The camera should request only the USB bandwidth it needs, rather than
attempting to request all USB bandwidth.
\end{itemize}

The Logitech C920 webcam satisfies these requirements and was used for the
prototype systems. Infrared filter removal with this camera is described in
Chapter \ref{c920}.

\section*{Infrared LED Mounting}

An infrared LED is bonded to each camera to allow individual camera feeds
to be synchronized with high accuracy via strobe flashes. This LED should
not obstruct the scene, but should still be within the camera's field of
view for all video resolutions of interest.

The recommended procedure for mounting LEDs is to set up a video feed from
the camera, apply cyanoacrylate glue (``super glue'') to the camera case,
hold the LED mounting rod in position until the glue sets (using the video
feed to guide placement), and then to apply two-part epoxy for a more
permanent bond.

For the Logitech C920, positioning the LED in the upper left corner of the
field of view when using a 4:3 resolution guarantees that it is visible in
all video modes (4:3 and 16:9).

The parts needed to add LEDs to each camera are as follows:

\begin{tabular}{llll}\hline
Qty & Description & Manuf. p/n & Digikey p/n \\
\hline
1 & NIR LED 940nm & SLED-56-16639 & SLED-56-16639-ND \\
1 & BNC female to wire & BU-P4969 & 314-1190-ND \\
\hline
\end{tabular}

Mechanical details for mounting LEDs to Logitech C920 cameras are shown
below:



The result is shown below:
\begin{center}
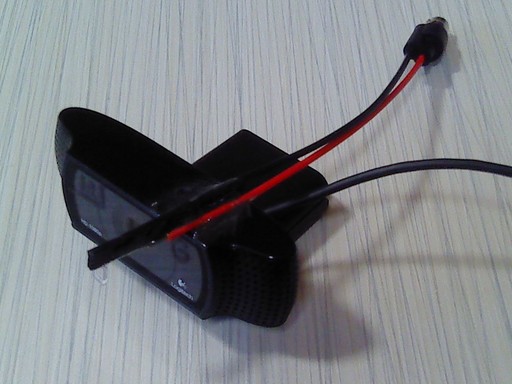
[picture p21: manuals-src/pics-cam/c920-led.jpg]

\end{center}

%
% This is the end of the file.

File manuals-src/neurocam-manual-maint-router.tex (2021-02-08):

% NeuroCam manual - Router.
% Written by Christopher Thomas.
% Copyright (c) 2021 by Vanderbilt University. This work is released under
% the Creative Commons Attribution-ShareAlike 4.0 International License.

\chapter{Router}
\label{router}

The NeuroCam computer, the game machine, and user machines talk to each other
via a wireless router. Any modern router should be suitable.

All routers have different configuration interfaces, so consult the router's
manual for information on performing any given step.

The following configuration steps must be performed:
\begin{itemize}
%
\item \textbf{Reset to factory defaults if necessary.}

This can be done by holding down a small button on the rear or underside of
the router. \textbf{Do not do this after the router is configured} -- it will
undo all configuration, and it will all have to be done again.

\item \textbf{Update router firmware if necessary.}

This is done by downloading the new router firmware to a USB stick and
following the directions in the router's manual.

\item \textbf{Log into the router.}

This is done by connecting a notebook or desktop computer to one of the
router's LAN ports, and pointing a web browser to the IP address written on
the bottom of the router. This is usually ``\verb+http://192.168.1.1+''.

\item \textbf{Set the administrator password.}

The default login and password are written on a sticker on the router. These
are usually both set to ``\verb+admin+''. NeuroCam systems are configured to
use the login ``\verb+admin+'' and the password ``\verb+administrator+''.

\textbf{This is easily guessed, and so should be changed when the system is
installed per Chapter \ref{setup}.}

\item \textbf{Set the wireless SSID and password.}

The SSID is the name of the wireless network provided by the router. For
NeuroCam machines, this should have the form ``\verb+neurocam-NN+'', for
some unique number ``\verb+NN+''. Routers that offer 2.4~GHz and 5~GHz
networks separately should use the names ``\verb+neurocam-NN-2.4GHz+'' and
``\verb+neurocam-NN-5GHz+'' for those networks.

The wireless password should be set to ``\verb+neurocam+'' for new NeuroCam
systems. \textbf{This is easily guessed, and so should be changed when the
system is installed per Chapter \ref{setup}.}

\textbf{NOTE: Routers that offer 2.4~GHz and 5~GHz networks may need the
password to be set for each separately. Make sure both are set!}

\item \textbf{Enable and configure MAC address filtering.}

To provide additional security, the router should be configured to use
whitelist--based MAC address filtering (``default deny'' or ``default to
block'' policy). This will only allow machines to connect if their network
cards belong to a list supplied during router configuration.

The MAC address of the machine being used to configure the router should be
added to the list before enabling filtering. If known, the MAC addresses for
other user machines may be added as well.

The MAC address of the NeuroCam machine and of the game machine will often
also have to be added. This depends on exactly how the router implements
filtering (some filter inbound wireless connections, others filter both
wireless and LAN connections). When in doubt, add the NeuroCam and game
machines to the whitelist.

To find the MAC address of a Linux machine, type ``\verb+ifconfig+''
(or ``\verb+/sbin/ifconfig+'') at a command prompt and look for the
``\verb+HWaddr+'' field.

\textbf{NOTE: Routers that offer 2.4~GHz and 5~GHz networks need MAC address
filtering set up separately, and saved, for each. Make sure it's set up for
both!}

\item \textbf{Add static IP assignments.}

The router normally dynamically assigns IP addresses to clients (including
the NeuroCam machine and the game machine).

Known machines can be assigned fixed IP addresses. At minimum the NeuroCam
machine should be given a fixed IP address. These usually take the form
``\verb+192.168.1.NN+'', where NN is the number of the NeuroCam computer.

\textbf{NOTE:} Some routers use a number other than ``\verb+1+'' in
``\verb+192.168.1.NN+''. Where possible, the DHCP configuration should be
changed to make this ``\verb+1+'', for consistency between installations.

\textbf{NOTE:} The router may have a ``device name''. This should be set
to ``\verb+neurocam-NN-gw+'' (where ``\verb+NN+'' is the same number from
the SSID, described above). The ``\verb+-gw+'' suffix guarantees that this
will not conflict with any NeuroCam computer name.

\item \textbf{Cover the WAN port (internet port).}

The NeuroCam system should never be connected to the internet, as it is not
hardened against attack. To avoid confusion between the WAN (internet) port
and the LAN (local network) ports, place a sticker or piece of tape over the
WAN port.
%
\end{itemize}

The preferred router for the NeuroCam prototype was as follows:

\begin{tabular}{llll}\hline
Qty & Description & Manuf. p/n & NewEgg SKU \\
\hline
%
1 & wireless router (a/b/g/n) & Asus RT-N66U & N82E16833320091 \\
%
\hline
\end{tabular}

%
%
\clearpage
\section{Asus RT-N66U Screenshots}

This is the Asus RT-N66U router (with tape over the WAN port):
\begin{center}
\begin{tabular}{ccc}
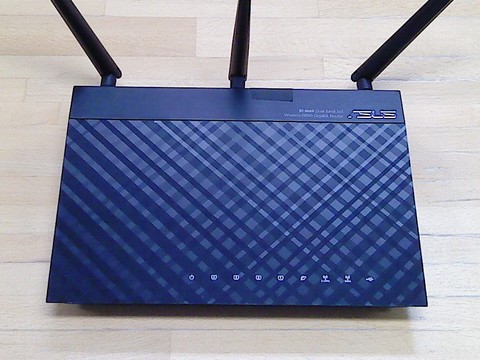
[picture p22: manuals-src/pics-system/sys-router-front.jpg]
 &
~ &
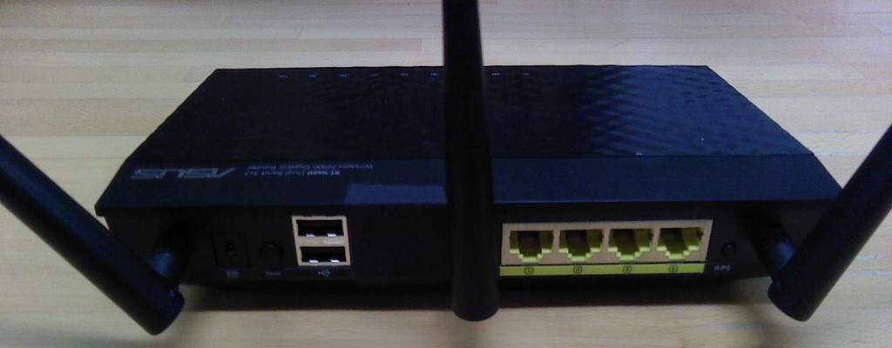
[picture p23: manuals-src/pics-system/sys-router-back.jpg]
 \\
\end{tabular}
\end{center}

Changing the administrator login/password (top section):
\begin{center}
\includegraphics[width=0.7\textwidth]
{pics-router/asus-n66u-admin-pw.png}
\end{center}

% Force a page break.
\clearpage
Setting the wireless network name (``SSID'') and password (``pre-shared 
key''):
\begin{center}
\includegraphics[width=0.7\textwidth]
{pics-router/asus-n66u-ssid.png}
\end{center}

Changing the MAC filter to whitelist mode (``accept the specified 
addresses''), and adding addresses:
\begin{center}
\includegraphics[width=0.7\textwidth]
{pics-router/asus-n66u-macfilter.png}
\end{center}

% Force a page break.
\clearpage
Assigning static IP addresses to specific machines:
\begin{center}
\includegraphics[width=0.7\textwidth]
{pics-router/asus-n66u-static.png}
\end{center}

%
%
\clearpage
\section{Installing OpenWrt}

\fixme{This hasn't been implemented, so no documentation for it.}

{\itshape The idea is to provide scripts that automatically configure and
compile the ``\verb+OpenWrt+'' open--source firmware. This lets us lock down
any features we don't want active, force an appropriate filtering mode, and
disable the web interface (which is one of the main security holes).

Implementing this is deferred, as it will be time--consuming.}

%
% This is the end of the file.

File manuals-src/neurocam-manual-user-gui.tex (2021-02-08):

% NeuroCam manual - GUI
% Written by Christopher Thomas.
% Copyright (c) 2021 by Vanderbilt University. This work is released under
% the Creative Commons Attribution-ShareAlike 4.0 International License.

\chapter{Web Interface}
\label{gui}

The NeuroCam system has three interface screens: The \textbf{configuration}
screen, the \textbf{monitoring} screen, and the \textbf{repository browser}.
The monitoring screen is seen when the system is collecting data. When the
system is not collecting data, the configuration screen and the repository
browser are both available.

\textbf{Important:} Do not use the ``back'' button of your web browser to
switch pages. This will result in stale CGI information being submitted.
Use the navigation buttons in the NeuroCam application instead.

\section{Configuration Screen}
\label{gui-config}

\begin{figure}[h]
\begin{center}
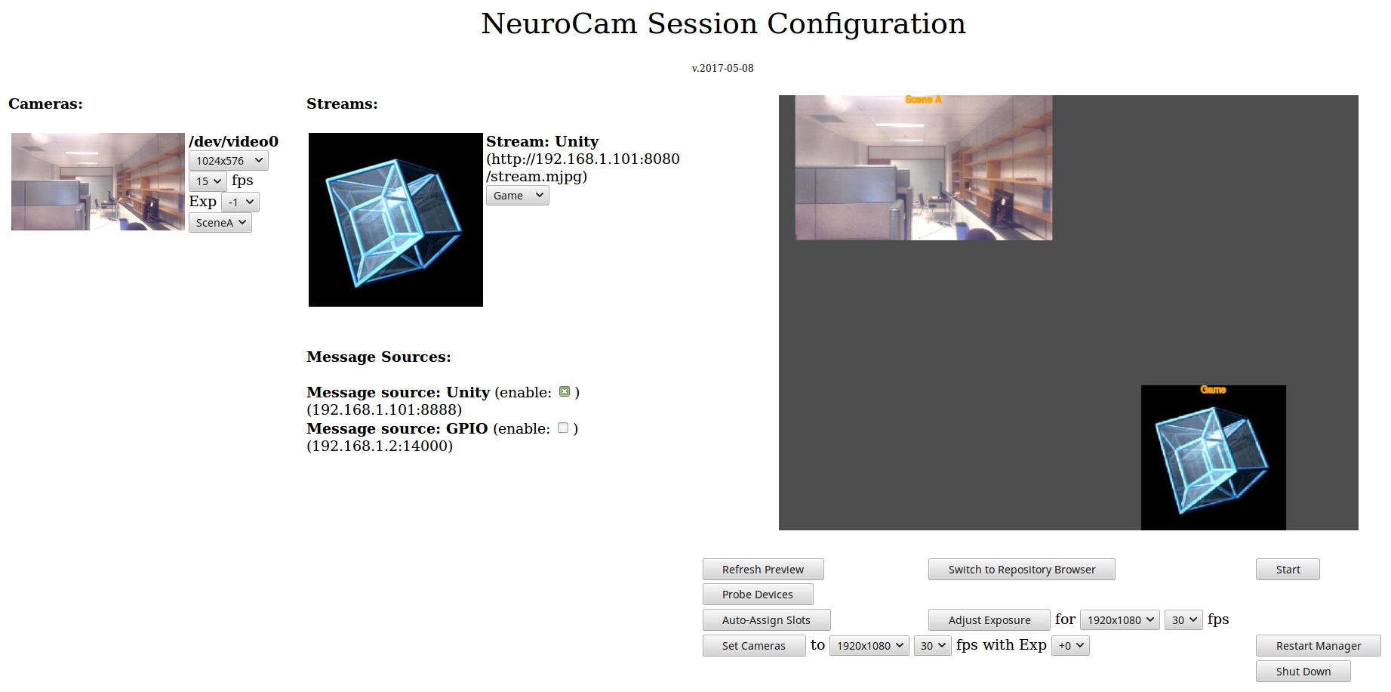
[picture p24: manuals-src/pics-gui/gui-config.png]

\end{center}
\caption{Configuration screen.}\label{fig-gui-config}
\end{figure}

% FIXME - Annotate the image.

The configuration screen is used to set up a new video capture session.

Detected cameras are shown in the left column. The middle column shows
detected computer video streams and detected event message sources. The
right column shows a still-frame preview of the video feeds, with a control
panel under the preview.

Each camera has resolution, frame rate, and exposure settings, along with a
still-frame preview of its input. Longer (positive) exposures give a brighter
image but may reduce frame rate; shorter (negative) exposures give a dimmer
image but may increase frame rate. The ``slot'' to which the camera feed is
assigned may also be changed.

Camera settings may be changed all at once using the ``Set Cameras to...''
control in the control panel.

Camera settings may also be adjusted using the ``Adjust Exposure for...''
control in the control panel. This reduces exposure and resolution for each
camera until the specified frame rate is achieved. \textbf{Note:} this
adjustment takes several minutes (up to tens of minutes if the system has
difficulty finding appropriate settings).

There should always be at least one computer video stream, representing
a ``screencast'' of the game the subject is playing.

There should always be at least two event message sources: one from the game
computer (which sends game-time synchronization messages), and one from the
GPIO-and-synch box (which sends camera LED synchronization messages and
messages indicating changes in its TTL inputs).

The NeuroCam interface tries to enable appropriate message sources, choose
acceptable resolutions and frame rates, and assign appropriate feeds to
appropriate slots in the composite image, but some manual adjustment is
usually necessary. The ``Auto-Assign Slots'' control in the control panel
can be used to reset this assignment to the default.

The ``Refresh Preview'' button can be used to capture new images from the
cameras and computer video sources and to redraw the composite image preview.

\textbf{NOTE:} Some browsers may fail to update the preview images due to
cache behavior. Wait a moment and then click the ``preview'' button again
to refresh these images.

The ``Probe Devices'' button can be used to re-detect cameras, computer video
streams, and event/message feeds.

The ``Switch to Repository Browser'' button changes to the repository browser
screen, saving the configuration for later editing.

The ``Start'' button creates a new session directory, activates video capture,
and switches to the monitoring screen. This may alternatively be done by
raising the ``start capture'' TTL line.

The ``Restart Manager'' button forcibly restarts the NeuroCam software. This
allows recovery if any part of the NeuroCam software stops behaving correctly.
This is also needed if performing a software update without restarting the
NeuroCam machine.

The ``Shut Down'' button turns off the NeuroCam computer.

\section{Monitoring Screen}
\label{gui-monitor}

\begin{figure}[h]
\begin{center}
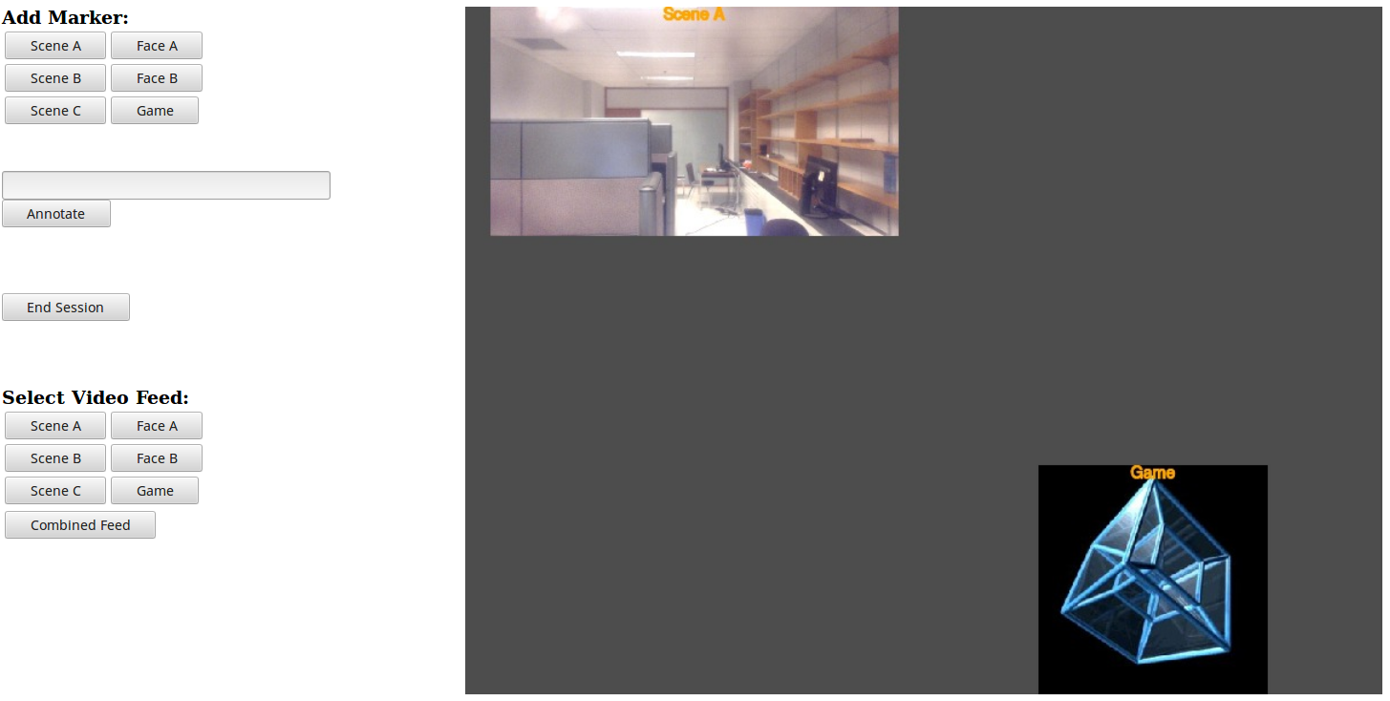
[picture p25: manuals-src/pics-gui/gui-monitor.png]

\end{center}
\caption{Monitoring screen.}\label{fig-gui-monitor}
\end{figure}

% FIXME - Annotate the image.

The monitoring screen is used to view the progress of a capture session that
is underway, and to add event markers to the log file for this session.

The ``Add Marker'' buttons produce timestamped log entries indicating
events of interest in their respective video feeds.

The ``Annotate'' button produces a timestamped log entry containing
user-supplied text.

The ``End Session'' button stops video capture, closes the log file, and
switches to the repository browser screen. This may alternatively be done
by raising the ``stop capture'' TTL line.

The ``Select Video Feed'' buttons replace the combined image with the raw
video frames from the selected feed. This is usually better-quality and 
faster than the combined feed. The ``Combined Feed'' button returns to the
composite feed.

\section{Repository Browser}
\label{gui-repo}

\begin{figure}[h]
\begin{center}
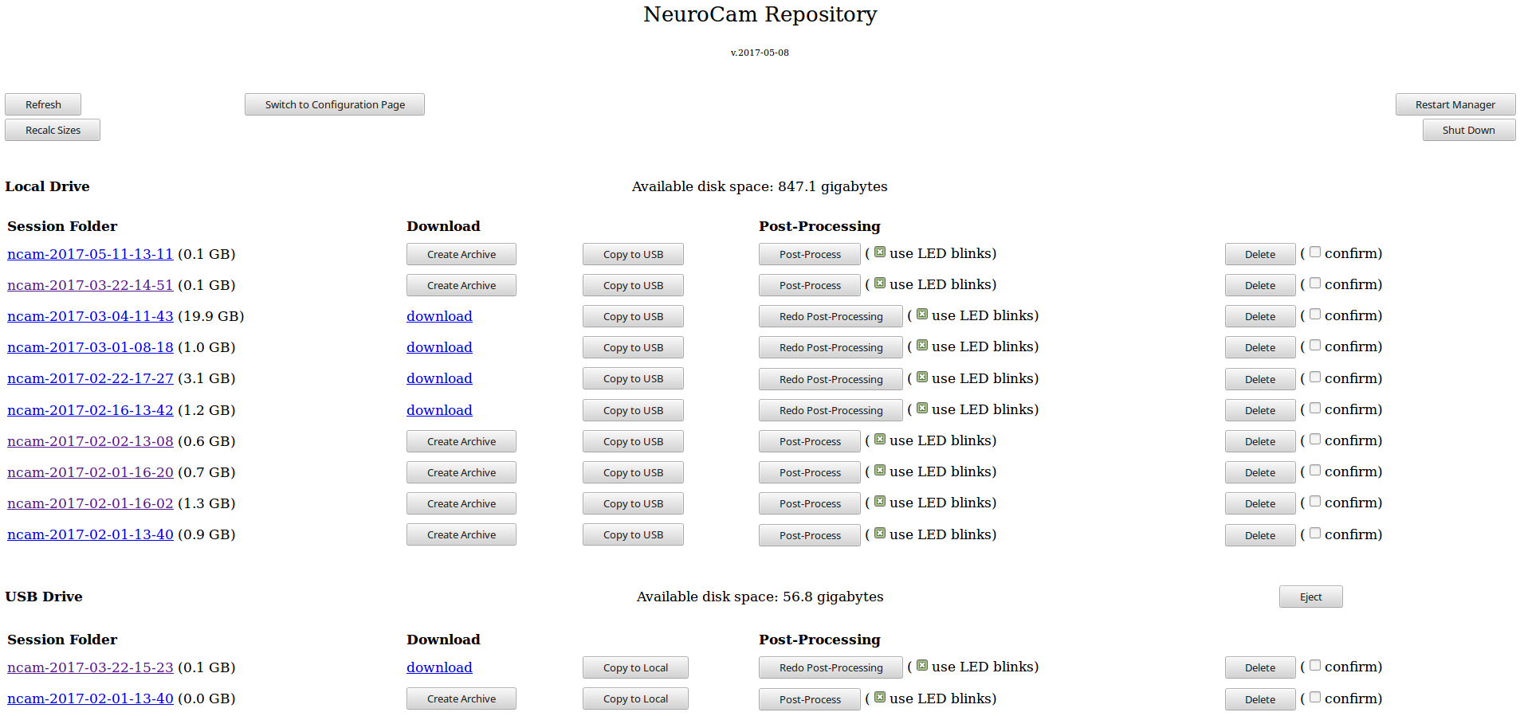
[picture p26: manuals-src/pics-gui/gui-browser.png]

\end{center}
\caption{Repository browser.}\label{fig-gui-repo}
\end{figure}

% FIXME - Annotate the image.

The repository browser is used to inspect the data files produced by
past sessions, to perform post-processing of session data, and to download
and transfer packaged session data. Old sessions may also be deleted to free 
up disk space.

The ``Session Folder'' column lists sessions within the repository. Clicking
on a session name opens that session's directory in a new window. Files may
be individually inspected and downloaded via that window. See Chapter 
\ref{repo} for a description of the repository folder contents.

The ``Download'' column contains a link to a ``.tar'' archive containing
a session's entire directory tree. This is intended to provide an easy way
to transfer a session's data over the network. The archive is created using 
the ``Create Archive'' button. If post-processing has been performed, the 
archive includes the post-processed files. \textbf{NOTE:} The archive file 
is large. Check that there is sufficient free space before creating it.

The ``Copy to USB'' and ``Copy to Local'' buttons create duplicates of their
session folders on a USB-attached drive and on the local drive, respectively.
\textbf{NOTE:} These may instead be named ``Move to USB'' and ``Move to 
Local'', depending on settings. ``Move'' deletes the original folder, while
``Copy'' leaves it in place.

The ``Post-Processing'' button triggers several operations on a session 
folder. If the ``use LED blinks'' checkbox is set, video timestamps are
synchronized with each other using flashes of the infrared LEDs. A new log
file is saved with these adjusted timestamps. After synchronization, a
``Composite'' video feed is created, arranged in the same manner as the 
monitoring feed but at higher resolution and with full frame rate. A new log
file is saved with composite feed frame events added. Finally, movie files
of all video feeds are created for easy preview/playback.
\textbf{NOTE:} Post-processing operations take a lot of time on the local
drive (a solid-state drive), and even longer on magnetic platter or flash
drives.

\fixme{Benchmark post-processing. How long does processing an hour of
five-camera-plus-game footage take?}

The ``Delete'' buttons allow individual session folders (and their archives)
to be removed. This cannot be undone; to prevent accidental deletion, the
corresponding ``confirm'' checkbox must be checked before pressing the
``Delete'' button. Deleting old sessions will need to be performed frequently
in order to free up disk space.

The ``Eject'' button unmounts an external drive so that it can be safely
removed. \textbf{NOTE:} Writing data to an external drive can take a while,
so please wait until the NeuroCam indicates that it is safe for the drive
to be removed.

The ``Refresh'' button re-scans the repository directory for new sessions.

The ``Recalc Sizes'' button recomputes metadata for all session folders.
\textbf{NOTE:} This can take a while, as each session may contain millions
of files.

The ``Switch to Configuration Page'' button changes to the configuration
screen, so that the next capture session may be set up.

The ``Restart Manager'' button forcibly restarts the NeuroCam software. This
allows recovery if any part of the NeuroCam software stops behaving correctly.
This is also needed if performing a software update without restarting the
NeuroCam machine.

The ``Shut Down'' button turns off the NeuroCam computer.

%
% This is the end of the file.

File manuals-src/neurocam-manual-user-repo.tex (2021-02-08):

% NeuroCam manual - Repository Data
% Written by Christopher Thomas.
% Copyright (c) 2021 by Vanderbilt University. This work is released under
% the Creative Commons Attribution-ShareAlike 4.0 International License.

\chapter{Repository Data}
\label{repo}

NeuroCam session data is stored in a ``repository''. Each session has its
own timestamped repository folder, containing some or all of the following:

\begin{itemize}

\item Raw video capture frames, stored as JPEG images in the ``Scene''
and ``Face'' folders.
\item Raw game capture frames, stored as JPEG images in the ``Game'' folder.

\item A ``Monitor'' folder containing reduced-size composited frames that
were sent to the monitoring GUI during the experiment. The composited frames
are not necessarily synchronized with each other.

\item A ``Composite'' folder containing larger composited frames produced
during post-processing. These composited frames should be synchronized.

\item A ``\verb+session.cfg+'' file containing information about the
settings used for the capture session. This file is described in detail in
Chapter \ref{structs}.

\item A ``\verb+logfile.txt+'' file containing raw event data (frame times,
user-supplied markers, and so forth).

\item Post-processed log files ``\verb+logfile-timed.txt+'' and
``\verb+logfile-composited.txt+''. The ``\verb+-timed+'' file has properly
synchronized timestamps and the ``\verb+-composited+'' file includes
timestamps for the ``Composite'' video stream (properly synchronized).

\item Several ``\verb+.mp4+'' compressed video files corresponding to the
video frame folders described above. These are lower-fidelity copies intended
to simplify review of footage.

\end{itemize}

% FIXME - Force a page break.
\clearpage
A typical session folder before post-processing is shown below:
\begin{center}
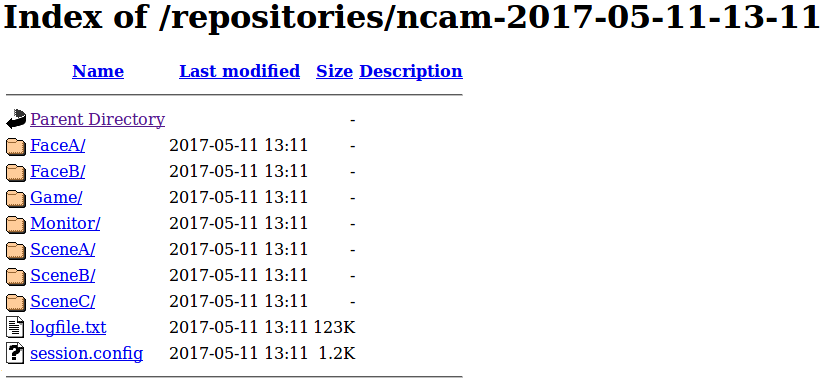
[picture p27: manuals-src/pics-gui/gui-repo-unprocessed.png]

\end{center}

A typical session folder after post-processing is shown below:
\begin{center}
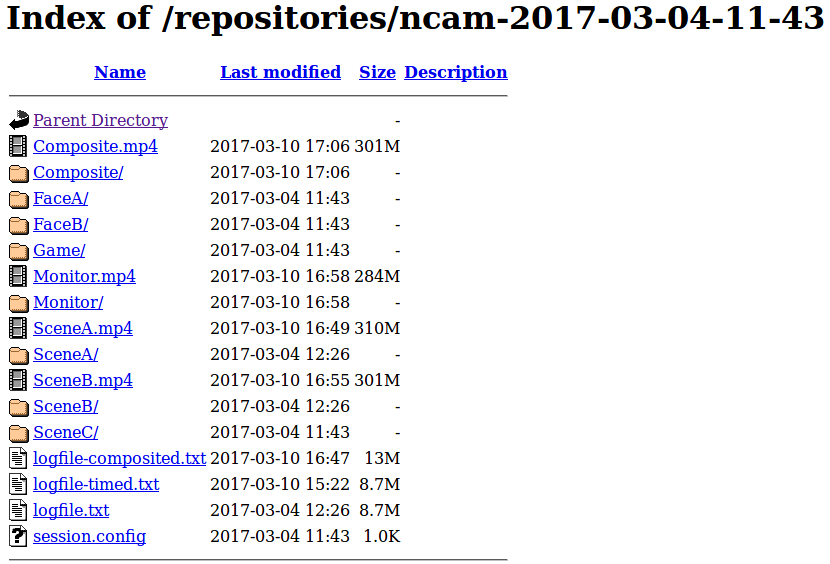
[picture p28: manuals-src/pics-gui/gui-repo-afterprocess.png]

\end{center}

% FIXME - Force a page break.
\clearpage
\section{Log File Format}

The logfile is a human-readable text file recording one event per line. The 
following types of event are recorded:
\begin{itemize}
\item \textbf{Frame events}, indicating that a video frame was recorded.
This may be from a camera, from a remote computer video feed, or from a
generated feed like the ``Monitor'' and ``Composite'' feeds.
\item \textbf{Network message events}, which are typically sent by the
GPIO-and-synch box or by external applications such as the game.
\item \textbf{Local GUI events}, which are either user annotations, user
markers, or instructions to change the monitoring display.
\end{itemize}

\textbf{Frame events} indicate arrival time, stream ``slot'' name, sequence 
number, and the filename (including subfolder) where the frame was saved. 
Typical frame events are as follows:
\begin{verbatim}
(1367) [SceneA]  frame 8  SceneA/00000008.jpg
(1374) [SceneB]  frame 16  SceneB/00000016.jpg
(1382) [Monitor]  frame 36  Monitor/00000036.jpg
(1403) [SceneB]  frame 17  SceneB/00000017.jpg
(1417) [Monitor]  frame 37  Monitor/00000037.jpg
(1437) [SceneA]  frame 9  SceneA/00000009.jpg
(1444) [SceneB]  frame 18  SceneB/00000018.jpg
\end{verbatim}

\textbf{Netowrk events} indicate arrival time, IP and port of the source,
and a message string. Typical network events are as follows:
\begin{verbatim}
(304) [192.168.1.101:8888]  MSG Unity timestamp 53284 ms
(1303) [192.168.1.101:8888]  MSG Unity timestamp 54283 ms
(2303) [192.168.1.101:8888]  MSG Unity timestamp 55283 ms
(2795) [192.168.1.2:14000]  MSG gpio A0 O: 01
(2815) [192.168.1.2:14000]  MSG gpio A0 O: 00
(3303) [192.168.1.101:8888]  MSG Unity timestamp 56283 ms
(4303) [192.168.1.101:8888]  MSG Unity timestamp 57283 ms
\end{verbatim}

\textbf{Local GUI events} indicate event time, the fact that the event was
local, and a command, annotation, or marker string. Typical local events
are as follows:
\begin{verbatim}
(23197) [local]  CMD monitor SceneA
(39396) [local]  Marker: Game
(48249) [local]  CMD monitor Game
(76264) [local]  CMD monitor SceneA
(104119) [local]  CMD monitor Monitor
(491174) [local]  User annotation: "task started"
\end{verbatim}

%
% This is the end of the file.

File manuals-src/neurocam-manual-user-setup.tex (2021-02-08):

% NeuroCam manual - Hardware Setup
% Written by Christopher Thomas.
% Copyright (c) 2021 by Vanderbilt University. This work is released under
% the Creative Commons Attribution-ShareAlike 4.0 International License.

\chapter{Hardware Setup}
\label{setup}

The NeuroCam system has several hardware components:

\begin{itemize}

\item One ``NeuroCam'' embedded computer. This performs data collection and
storage.

\item One wireless router. This is connected to the NeuroCam computer and
to the game machine via wired LAN, and accepts wireless connections from
user machines. \textit{Do not connect this to the internet.}

The router used by the prototype system was an \mbox{Asus RT-N66U}.

\item One GPIO-and-synchronization box. This is connected to the NeuroCam
computer via USB, and provides TTL synchronization outputs over BNC and
accepts TTL-level inputs via a ribbon cable.

Any change in the TTL inputs is reported (and logged). A low-to-high
transition on bit 7 will start the NeuroCam recording, and a low-to-high
transition on bit 6 will stop recording (with a ``dead time'' of ten seconds
before further commands will be recognized). Input bits 0--5 are logged but
do not change NeuroCam behavior, and may be used for any desired purpose.

\item Five cameras, connected to the NeuroCam computer via USB.

The camera model used by the prototype system was the Logitech C920.

\end{itemize}

\begin{center}
% Black magic for the sizes here.
\begin{tabular}{cccc}
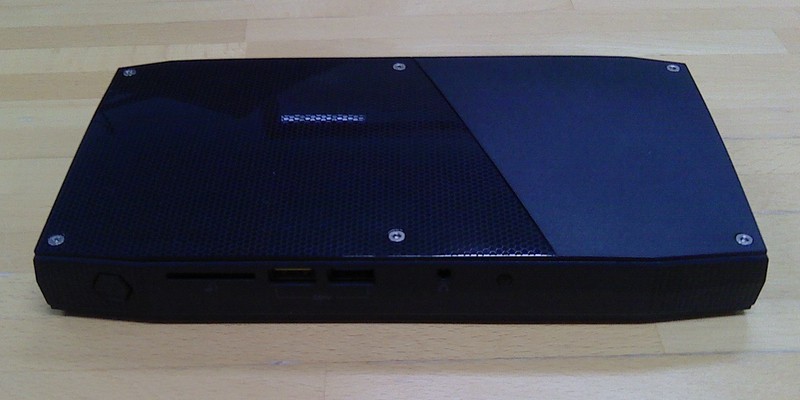
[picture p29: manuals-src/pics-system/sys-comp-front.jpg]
 &
 &
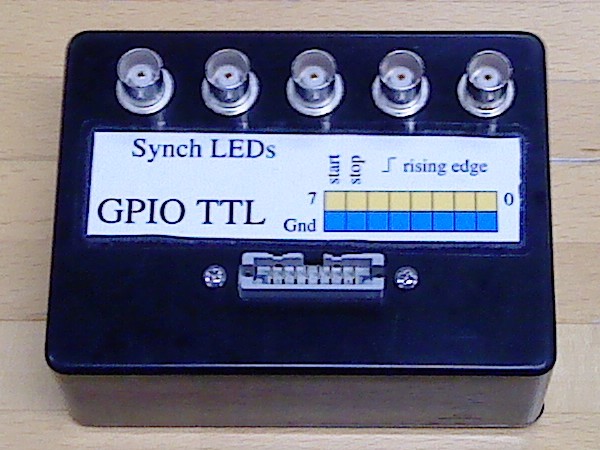
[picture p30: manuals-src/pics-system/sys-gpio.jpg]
 &
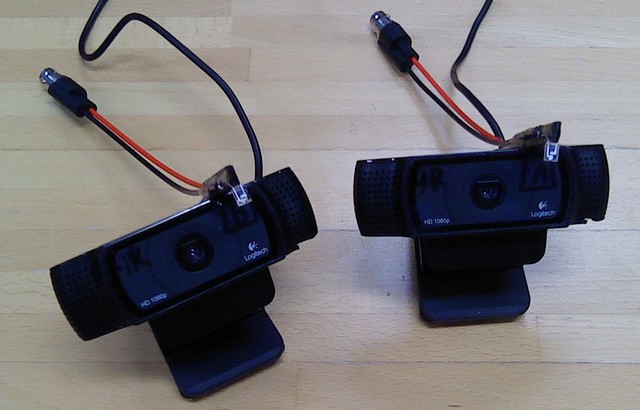
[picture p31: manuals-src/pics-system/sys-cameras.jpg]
 \\
\end{tabular}
\end{center}

\clearpage

There are several tasks of note that have to be performed in order to
configure the NeuroCam hardware for use:

\begin{itemize}

\item The camera synchronization LEDs must be connected to the
GPIO-and-synchronization box via BNC cables.

Alternatively, a TTL-controlled lamp (visible or IR) may be placed in the
scene within view of all cameras and connected to the GPIO-and-synchronization
box.

\item The administrator password for the wireless router \textit{must} be
set to a new, stronger value. The default password (``administrator'') is
provided strictly for setup purposes.

The password for the NeuroCam network should also be changed. The default
password (``neurocam'') is easily guessed from the network name.

\item Any machines that are intended to communicate wirelessly with the
NeuroCam system must be added to the wireless router's MAC whitelist.
Machines that communicate via network cable may also need to be added,
depending on the router's configuration.

\item The game machine must be configured to stream MJPEG video, and to
respond to NeuroCam queries about offered content. The ``\verb+VLC+''
application was used for MJPEG streaming in the prototype system. Consult
VLC's documentation for further information.

Network handshaking with the game machine is described in Chapter 
\ref{handshake}.

\end{itemize}

The wireless router may be reconfigured by connecting to a wired LAN port
and accessing the web address printed on the bottom of the device.
\textbf{Do not} reset the device to factory default settings; this will lose 
all NeuroCam-related configuration.

See Chapter \ref{router} for details about configuring routers.

%
% This is the end of the file.

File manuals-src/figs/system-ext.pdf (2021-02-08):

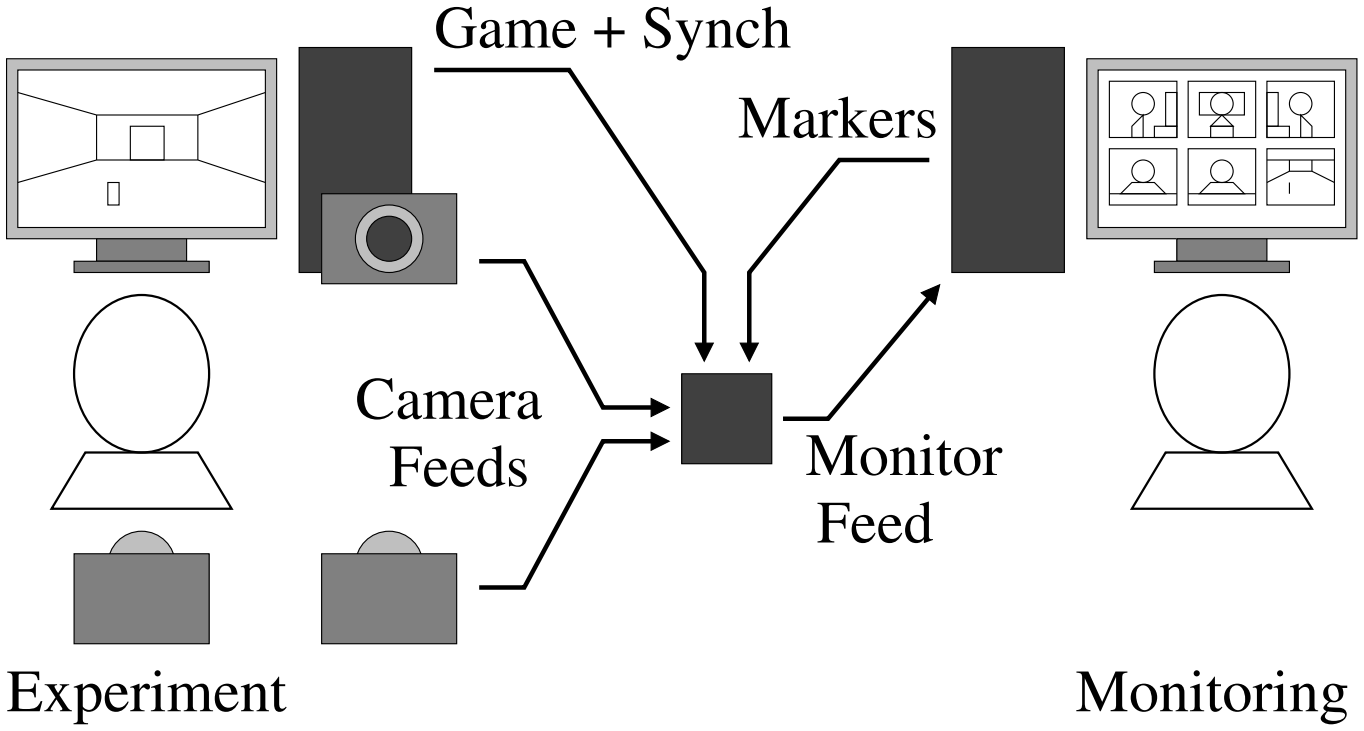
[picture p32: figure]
Camera; Feeds; Monitor; Feed; Game + Synch; Experiment; Monitoring; Markers
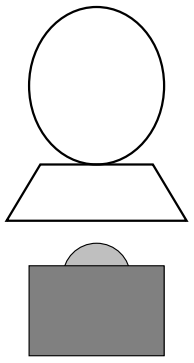
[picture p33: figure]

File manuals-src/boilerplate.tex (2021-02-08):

% NeuroCam manual - License tagline.
% Written by Christopher Thomas.
% Copyright (c) 2021 by Vanderbilt University. This work is released under
% the Creative Commons Attribution-ShareAlike 4.0 International License.
Copyright (c) \the\year\ by Vanderbilt University. This work is released under
the Creative Commons Attribution-ShareAlike 4.0 International License.
%
% This is the end of the file.

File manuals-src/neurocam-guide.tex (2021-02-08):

% NeuroCam manual - User guide subset - Top level
% Written by Christopher Thomas.
% Copyright (c) 2021 by Vanderbilt University. This work is released under
% the Creative Commons Attribution-ShareAlike 4.0 International License.

\documentclass[letterpaper,11pt]{report}
\usepackage[letterpaper]{geometry}
\usepackage{graphicx}
\usepackage{verbatim}

\geometry{nohead,footskip=0.3in,margin=0.75in}

% Force my paragraph style, darnit.
\usepackage{indentfirst}
\setlength{\parskip}{\baselineskip}

% Custom macros.
\newcommand{\fixme}[1]{\textbf{FIXME: #1}}

% Document body.
\begin{document}

% Title page.

\pagestyle{empty}

\begin{center}
%
\vspace*{1.5in}
{\Huge NeuroCam System User Guide} \\
{\footnotesize Written by Christopher Thomas -- \today.} \\
%
\vspace*{1in}
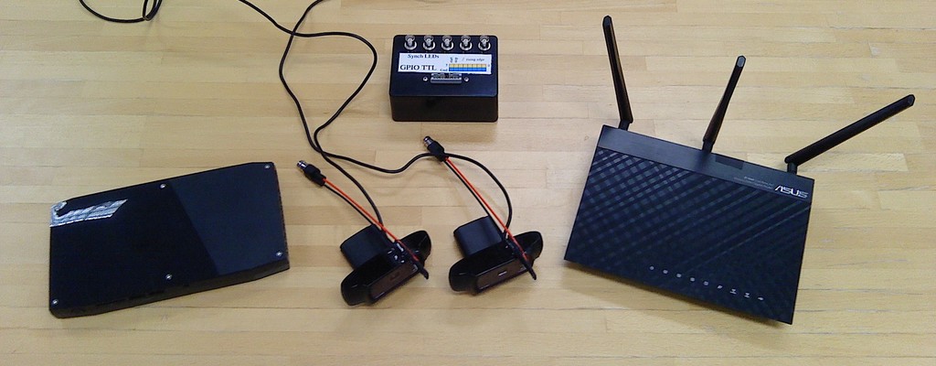
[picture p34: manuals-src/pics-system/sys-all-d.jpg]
 \\
%
\vfill
{\footnotesize \input{boilerplate}}
%
\end{center}
%
\clearpage
%
\pagestyle{plain}
\pagenumbering{roman}
\setcounter{page}{1}
%
\tableofcontents
%
\clearpage
\pagestyle{plain}
\setcounter{page}{1}
\pagenumbering{arabic}
% NOTE - "\thispagestyle" is used for part and chapter beginning pages,
% and overrides \pagestyle.
% Redefine it to be harmless.
% NOTE - The canonical solution ("\pagenumbering{gobble}") resets the page
% counter whenever it's used.
\renewcommand{\thispagestyle}[1]{}

% Part 1: User guide.
\iffalse
%
\clearpage
\pagestyle{empty}
\part{Using the NeuroCam System}
\pagestyle{plain}
%
\fi

\input{neurocam-manual-user-intro}
\input{neurocam-manual-user-setup}
\input{neurocam-manual-user-gui}
\input{neurocam-manual-user-repo}
\input{neurocam-manual-user-handshake}

% FIXME - We need the router information too.
% This is normally in the maintenance section.
\input{neurocam-manual-maint-router}

\end{document}

%
% This is the end of the file.

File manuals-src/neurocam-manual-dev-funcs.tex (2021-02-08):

% NeuroCam manual - Library Functions
% Written by Christopher Thomas.
% Copyright (c) 2021 by Vanderbilt University. This work is released under
% the Creative Commons Attribution-ShareAlike 4.0 International License.

\chapter{Library Functions}
\label{funcs}

\fixme{Content goes here.}

This should give an overview of how libraries are split up, and an overview 
of the functions offered by each library.

While the function and variable lists can be more or less the extracted 
declarations and comments, there should be a preamble for each library 
explaining how all of the pieces fit together and are intended to be used.

%
% This is the end of the file.

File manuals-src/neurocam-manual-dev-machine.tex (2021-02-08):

% NeuroCam manual - Development Computer
% Written by Christopher Thomas.
% Copyright (c) 2021 by Vanderbilt University. This work is released under
% the Creative Commons Attribution-ShareAlike 4.0 International License.

\chapter{Development Computer}
\label{devmachine}

The NeuroCam development environment is an x86-architecture computer running
the Linux Mint operating system, with the NeuroCam software and its required
support packages installed.

Hardware specifications are not critical, but if more than two cameras are to
be tested on a development machine, hardware performance comparable to the 
NeuroCam computer described in Chapter \ref{machine} will be needed.

To build a new NeuroCam development computer, you will need the following:
\begin{itemize}
%
\item A suitable computer.
\item A USB stick containing the Linux Mint 18.1 installer.
\item A USB stick containing the NeuroCam installer and the NeuroCam
development environment.
%
\end{itemize}

Making a NeuroCam development environment USB stick is described in Section
\ref{devmachine-usb}. Making a NeuroCAM install USB stick is described in
Section \ref{machine-usb}. Both of these may be placed on the same USB stick.

Making a Linux Mint install USB stick is described in Section
\ref{machine-usbmint}.

%
%
\section{First-Time Installation}

This is a variation of the procedure used for NeuroCam computers. There are
important differences, so be sure to check the steps closely.

\fixme{This uses the NeuroCam computer install scripts, which require the
username ``neurocam-admin''. Dedicated dev scripts would relax that
requirement.}

To install Linux and the NeuroCam software (but not the development
environment):
\begin{itemize}
%
\item Connect the machine to a keyboard, a mouse, and a monitor.
\item With the machine unpowered, plug in the Mint 18.1 USB stick.
\item Turn on the machine.
\item Get to the BIOS menu by holding the appropriate key during boot
(usually F2).
\item Turn UEFI off. This may be called ``Windows compatibility''.
\item Edit the boot order, moving the USB stick to the top.
\item Hit F10 to save and exit.
%
\item (The machine should now show the Linux boot menu.)
\item From the Linux boot menu, pick ``start in compatibility mode''.
\item From the GUI, open a terminal window.
\item Type ``\verb+sudo bash+'' to get a root session.
\item Type ``\verb+fdisk /dev/sda+'' to partition the drive.
\item Delete any existing partitions. The normally won't be any.
\item Create a 50 gigabyte partition (for the OS), an 8 gigabyte partition
(for swap space), and a third partition (for data).
\item Set the OS and data partitions to type 83 (Linux; this may be set
already by default). Set the swap partition to type 82 (Linux swap).
\item Set the ``bootable'' flag on the OS partition.
\item Save and exit \verb+fdisk+.
\item Type ``\verb+mke2fs -j /dev/sda1+'' and
``\verb+mke2fs -j -m 0 /dev/sda3+'' to create filesystems on the OS and
data partitions, respectively.
\item Type ``\verb+mkswap /dev/sda2+'' to initialize the swap partition.
\item Type ``\verb+exit+'' twice to leave the root shell and the terminal
window.
%
\item Click ``Install Linux Mint''.
\item Do not set up networks.
\item Do not install proprietary software.
\item Select ``Something Else'' for the target partition.
\item Doubleclick ``\verb+/dev/sda1+'', select ``use as ext3 journaling
filesystem'', check ``format'', and select mount point ``/''.
\item Doubleclick ``\verb+/dev/sda2+'', and select ``use as swap area''.
\item Doubleclick ``\verb+/dev/sda3+'', select ``use as ext3 journaling
filesystem'', check ``format'', and select mount point ``/data''.
\item Click ``Install Now''.
\item Select time zone and keyboard type.
\item For ``Your Name'', enter ``NeuroCam Developer''. Enter any desired
name for ``Your Computer's Name'' (allowable characters are lower--case 
letters, numbers, and hyphen; no whitespace, capitals, or punctuation).
For ``Pick a User Name'', enter ``\verb+neurocam-admin+''. For the password,
enter ``\verb+neurocam+''.
\par
\textbf{This password is easily guessed, and so should be changed when
setup is completed.} The procedure for changing passwords is described in
Section \ref{machine-password}.
\item Check ``require password to log in''.
\item Begin the install.
\item When the installation finishes, click ``restart now''.
\item Remove the USB stick when the system reboots.
%
\item (The system should boot to the Linux Mint login screen.)
\item Log in as ``\verb+neurocam-admin+'' with the password
``\verb+neurocam+''.
\par
\textbf{NOTE:} If the system does not let you log in with the credentials
supplied above, see Section \ref{machine-password} for the password reset
method.
%
\item (You should now be logged in as ``\verb+neurocam-admin+'' on a graphical
desktop.)
\item Click the terminal icon in the hotbar or start menu to get a terminal
window with a command shell.
\item In the terminal window, type ``\verb+sudo bash+'' to get a root shell.
Enter ``\verb+neurocam+'' as the \verb+sudo+ password.
\item Type ``\verb+passwd+'' to reset the \verb+root+ account's password.
Set it to ``\verb+administrator+''.
\par
\textbf{This password is easily guessed, and so should be changed when
setup is completed.} The procedure for changing passwords is described in
Section \ref{machine-password}.
\item Type ``\verb+exit+'' to leave the root shell.
\item Type ``\verb+exit+'' again to leave the command shell, closing the
terminal window.
\item Click on the ``log out'' icon in the start menu.
%
\item Press \verb+ctrl-alt-F6+ to get to a text console (if using a Mac
keyboard, \verb+ctrl-option-function-F6+).
\item Log in as ``\verb+root+'' with the password ``\verb+administrator+''.
\item Plug the development computer into an internet jack.
\item Wait 10 seconds.
\item Type ``\verb+ifconfig+'' to get network interface information. Wired
ethernet is the entry with a device name starting with ``\verb+e+'' (usually
``\verb+eth+'', ``\verb+eno+'', ``\verb+enp+'', or similar).
\item When network handshaking has finished, there will be an
``\verb+inet addr+'' field with an IP address assigned. This address will
\textbf{not} start with \verb+127+ (\verb+127.x.x.x+ is the loopback address).
\item Your institution's network may require network cards' MAC addresses
to be registered before allowing connections. To find the network card's MAC
address, look for a field named ``\verb+HWaddr+''. Write this down.
\item Type ``\verb+ping 8.8.8.8+'' to check internet connectivity. A response
of ``\verb+64 bytes from 8.8.8.8+'' means that the internet is visible.
\item Type ``\verb+mkdir /usb+'' to create a manual mount point for the USB
stick. This only needs to be done once.
\item Make sure no other USB sticks are in the machine, and insert a
NeuroCam update USB stick.
\item Type ``\verb+mount -t auto -o exec /dev/sdb1 /usb+'' to manually mount
the USB stick and to allow scripts to be run from the stick.
\item Type ``\verb+/usb/neurocam-install/scripts/do-install.sh+'' to perform
first-time NeuroCam software installation. This will take a while.
\par
\textbf{NOTE:} This should skip most confirmation steps, but may still ask for
user input. Default settings should always be acceptable.
\item Once this has finished, type ``\verb+shutdown -r now+'' to reboot.
\item Remove the USB stick when the system reboots.
%
\end{itemize}

To install the development environment:
\begin{itemize}
%
\item Allow the machine to boot to the graphical login screen as normal.
\par
(To switch from the text logon screen to the graphical screen, press
\verb+ctrl-alt-F8+; on a Mac keyboard, \verb+ctrl-option-function-F8+.)
\item Log in as ``\verb+neurocam-admin+''.
\item Make sure no other USB sticks are in the machine, and insert a NeuroCam
development USB stick. Close the file browser popup window, if any.
\item Click the terminal icon in the hotbar or start menu to get a terminal
window with a command shell.
\item Navigate to the directory you wish to use as the development tree root.
You can create a new directory with ``\verb+mkdir ~/(directory)+'' and move
to it with ``\verb+cd ~/(directory)+''. Type ``\verb+pwd+'' to check that you
are in the desired location.
\item Type ``\verb+tar -xvf /media/neurocam-admin/(label)/neurocam/dev/*.tar+''.
\par
This refers Mint's automatic mount point for the USB stick, with 
``\verb+(label)+'' replaced with the stick's volume label (or serial number if
there is no volume label). You can use ``tab completion'' to avoid having to
type this: if only one USB stick is plugged in, 
``\verb+/media/neurocam-admin/(tab)+'' will automatically expand to the
correct mount point name when the \verb+tab+ key is pressed.
\item When the ``\verb+tar+'' command has finished extracting files, type
``\verb+ls+'' to check that the development tree's subdirectories are in 
place.
\item Type ``\verb+umount /media/neurocam-admin/(label)+'' to unmount the
USB stick for safe removal.
%
\end{itemize}

%
%
\section{Updating the Development Machine}

Linux will usually update itself automatically, but doing this manually is
also acceptable. The NeuroCam software and the NeuroCam development code
will have to be updated manually.

Updating Linux Mint requires an internet connection. Updating the NeuroCam
software and development code do not.

To update Linux Mint:
\begin{itemize}
%
\item (Turn on the machine and allow it to boot per normal.)
\item Press \verb+ctrl-alt-F6+ to get to a text console.
\item Log in as ``\verb+root+''.
\item Type ``\verb+ping 8.8.8.8+'' to check internet connectivity. A response
of ``\verb+64 bytes from 8.8.8.8+'' means that the internet is visible.
\item Type ``\verb+~/neurocam-scripts/do-mintupdate.sh+''. This may take a
while, depending on how many packages need to be updated.
\par
\textbf{NOTE:} This should skip most confirmation steps, but may still ask for
user input. Default settings should always be acceptable.
\item Type ``\verb+exit+'' to log out.
\item Press \verb+ctrl-alt-F8+ to return to the graphical login screen.
\end{itemize}

To update the NeuroCam software:
\begin{itemize}
%
\item (Turn on the machine and allow it to boot per normal.)
\item Press \verb+ctrl-alt-F6+ to get to a text console.
\item Log in as ``\verb+root+''.
\item Make sure no other USB sticks are in the machine, and insert a
NeuroCam update USB stick.
\item Wait five seconds, then type ``\verb+mount /usb+''.
\item Type ``\verb+~/neurocam-scripts/do-update.sh+''.
\item Once this has finished, type ``\verb+shutdown -r now+'' to reboot.
This will force a full restart of the NeuroCam software.
\item Remove the USB stick when the system reboots.
%
\end{itemize}

To update the NeuroCam development environment:
\begin{itemize}
\item (Turn on the machine and allow it to boot to the graphical login
screen as normal.)
\item Log in as ``\verb+neurocam-admin+''.
\item Make sure no other USB sticks are in the machine, and insert a NeuroCam
development USB stick. Close the file browser popup window, if any.
\item Click the terminal icon in the hotbar or start menu to get a terminal
window with a command shell.
\item Navigate to the directory you use as the development tree root.
Type ``\verb+pwd+'' to check that you are in the desired location.
\item \textbf{Make sure that you have backed up any changed files.}
Reinstalling the development tree will overwrite any existing files that are
present.
\item Type ``\verb+tar -xvf /media/neurocam-admin/(label)/neurocam/dev/*.tar+''.
\item When the ``\verb+tar+'' command has finished extracting files, type
``\verb+ls+'' to check that the development tree's subdirectories are in 
place.
\item Type ``\verb+umount /media/neurocam-admin/(label)+'' to unmount the
USB stick for safe removal.
\end{itemize}

%
%
\section{Making New Development USB Sticks}
\label{devmachine-usb}

The NeuroCam development environment can be added to any USB stick. This
does not interfere with existing data; the software is placed in a new
directory called ``\verb+neurocam-dev+''.

To add the install and update software to an already-formatted USB stick:
\begin{itemize}
\item On a NeuroCam development machine, open a terminal window.
\item Navigate to the NeuroCam development directory.
\item Make sure no other USB sticks are in the machine, and insert a USB
stick to turn into a NeuroCam update USB stick.
\item Type ``\verb+install/scripts/make-devkey.sh+''.
\item Wait until the script has finished.
\item Type ``\verb+umount /media/neurocam-admin/(label)+'' to unmount the
USB stick for safe removal.
\end{itemize}

%
% This is the end of the file.

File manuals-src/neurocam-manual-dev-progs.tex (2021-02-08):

% NeuroCam manual - Programs
% Written by Christopher Thomas.
% Copyright (c) 2021 by Vanderbilt University. This work is released under
% the Creative Commons Attribution-ShareAlike 4.0 International License.

\chapter{Executables}
\label{progs}

\fixme{Content goes here.}

This should give an overview of the internal architecture of each executable,
and then go on to describe variables and functions in the same manner as with
libraries.

%
% This is the end of the file.

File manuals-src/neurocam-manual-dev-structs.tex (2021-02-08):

% NeuroCam manual - Data Structures
% Written by Christopher Thomas.
% Copyright (c) 2021 by Vanderbilt University. This work is released under
% the Creative Commons Attribution-ShareAlike 4.0 International License.

\chapter{Data Structures}
\label{structs}

\section{Camera Configuration Structure}

\fixme{Content goes here.}

\section{Network Entity Configuration Structure}

\fixme{Content goes here.}

\section{Session Configuration Structure}

\fixme{Content goes here.}

\section{Networking Information Structure}

\fixme{Content goes here.}

\section{Configuration File Format}

\fixme{Content goes here.}

%
% This is the end of the file.

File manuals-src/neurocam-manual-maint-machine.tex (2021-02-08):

% NeuroCam manual - NeuroCam Computer
% Written by Christopher Thomas.
% Copyright (c) 2021 by Vanderbilt University. This work is released under
% the Creative Commons Attribution-ShareAlike 4.0 International License.

\chapter{NeuroCam Computer}
\label{machine}

The NeuroCam computer is a small--form--factor x86--architecture computer
running the Linux Mint operating system and the NeuroCam software.

To build a new NeuroCam computer, you will need the following:
\begin{itemize}
%
\item A suitable computer.
\item A USB stick containing the Linux Mint installer.
\item A USB stick containing the NeuroCam installer.
%
\end{itemize}

Details of the hardware and the installation process are described in their
appropriate sections. The procedure for making new USB sticks is also
described.

%
%
%
\section{Hardware}

The NeuroCam computer must be powerful enough to perform image compositing
in real-time, have a solid--state drive that is fast, large, and has high
endurance, and have enough RAM to handle any cacheing and buffering
transparently.

The components used for the NeuroCam prototype are as follows:

\begin{tabular}{llll}\hline
Qty & Description & Manuf. p/n & NewEgg SKU \\
\hline
%
1 & Intel NUC with Core i7 & Intel NUC6i7KYK & N82E16856102166 \\
% This is 1x 8 gig.
1 & DDR4 260-pin SO-DIMM 8G$^*$ & Ripjaws F4-2133C15S-8GRS & N82E16820232147 \\
% This is 2x 4 gig. We only _need_ 1x 4 gig.
%1 & DDR4 260-pin SO-DIMM 4G$^*$ & Ripjaws F4-2133C15D-8GRS & N82E16820232146 \\
1 & SSD 1 TB high-endurance M.2 & Samsung MZ-N5E1T0BW & N82E16820147567 \\
%
\hline
\multicolumn{4}{l}{$^*$A single 4-gig stick is sufficient, but no longer in
NewEgg's catalogue.} \\
\end{tabular}

To assemble the computer (Intel NUC version):
\begin{itemize}
%
\item Ensure that the workspace is free of clutter and clean.

\item Ensure that clothing is not carrying electrostatic charge. A humidifier
can reduce static electricity in the workspace if necessary.

\item Remove the skull-logo faceplate and set it aside. Unpack the plain
faceplate as a replacement.

\item With the machine interior exposed, carefully seat the RAM in the lower
DIMM slot. Apply \textbf{gentle} pressure until the latches engage to secure
the RAM. It may be necessary to open the latches by hand to fully insert the
RAM.

\item Remove the securing screw for the first solid-state drive slot, and
insert the solid-state drive. Ensure that the drive is seated firmly in its
connector, and reinstall the securing screw.

\item Reinstall the faceplate.
%
\end{itemize}

%
%
%
\section{Installing Mint and the NeuroCam Software}

The prototype NeuroCam machine used Linux Mint 18.1. This version or any later
version should have full driver support for the specific Intel NUC machine
described above.

You will need a Mint 18.1 install USB stick and a NeuroCam install USB stick.
Making these is described in Sections \ref{machine-usbmint} and
\ref{machine-usb}, respectively.

%
\subsection{First-Time Installation}

To install Linux and the NeuroCam software:
\begin{itemize}
%
\item Connect the machine to a keyboard, a mouse, and an HDMI monitor.
\item With the machine unpowered, plug in the Mint 18.1 USB stick.
\item Turn on the machine.
\item Hit F2 to get to the BIOS menu.
\item Turn UEFI off. This may be called ``Windows compatibility''.
\item Edit the boot order, moving the USB stick to the top.
\item Hit F10 to save and exit.
%
\item (The machine should now show the Linux boot menu.)
\item From the Linux boot menu, pick ``start in compatibility mode''.
\item From the GUI, open a terminal window.
\item Type ``\verb+sudo bash+'' to get a root session.
\item Type ``\verb+fdisk /dev/sda+'' to partition the solid--state drive.
\item Delete any existing partitions. The normally won't be any.
\item Create a 50 gigabyte partition (for the OS), an 8 gigabyte partition
(for swap space), and a third partition (for data).
\item Set the OS and data partitions to type 83 (Linux; this may be set
already by default). Set the swap partition to type 82 (Linux swap).
\item Set the ``bootable'' flag on the OS partition.
\item Save and exit \verb+fdisk+.
\item Type ``\verb+mke2fs -j /dev/sda1+'' and
``\verb+mke2fs -j -m 0 /dev/sda3+'' to create filesystems on the OS and
data partitions, respectively.
\item Type ``\verb+mkswap /dev/sda2+'' to initialize the swap partition.
\item Type ``\verb+exit+'' twice to leave the root shell and the terminal
window.
%
\item Click ``Install Linux Mint''.
\item Do not set up networks.
\item Do not install proprietary software.
\item Select ``Something Else'' for the target partition.
\item Doubleclick ``\verb+/dev/sda1+'', select ``use as ext3 journaling
filesystem'', check ``format'', and select mount point ``/''.
\item Doubleclick ``\verb+/dev/sda2+'', and select ``use as swap area''.
\item Doubleclick ``\verb+/dev/sda3+'', select ``use as ext3 journaling
filesystem'', check ``format'', and select mount point ``/data''.
\item Click ``Install Now''.
\item Select time zone and keyboard type.
\item For ``Your Name'', enter ``NeuroCam User''. For ``Your Computer's
Name'', enter ``\verb+neurocam-NN+'', where ``\verb+NN+'' is the number
assigned to this NeuroCam machine. For ``Pick a User Name'', enter
``\verb+neurocam-admin+''. For the password, enter ``\verb+neurocam+''.
\par
\textbf{This password is easily guessed, and so should be changed when the
system is installed per Chapter \ref{setup}.}
\item Check ``require password to log in''.
\item Begin the install.
\item When the installation finishes, click ``restart now''.
\item Remove the USB stick when the system reboots.
%
\item When booting to a new install, press \verb+ctrl-alt-F6+ to switch to
text console \#6 (1 through 6 are valid). If using a Mac keyboard, use
\verb+ctrl-option-function-F6+.
\item Log in as ``\verb+neurocam-admin+'' with the password
``\verb+neurocam+''.
\par
\textbf{NOTE:} If the system does not let you log in with the credentials
supplied above, see below for the password reset method.
%
\item (You should now be logged in as ``\verb+neurocam-admin+'' on a text
console.)
\item Type ``\verb+sudo bash+'' to get a root shell. Enter
``\verb+neurocam+'' as the \verb+sudo+ password.
\item Type ``\verb+passwd+'' to reset the \verb+root+ account's password.
Set it to ``\verb+administrator+''.
\par
\textbf{This password is easily guessed, and so should be changed when the
system is installed per Chapter \ref{setup}.}
\item Type ``\verb+exit+'' twice to leave the root shell and the console 
login session.
\item (You should now be at a console login prompt.)
\item Log in as ``\verb+root+'' with the password ``\verb+administrator+''.
\item Type ``\verb+nano /etc/default/grub+'' to edit the bootloader
configuration file.
\item Press \verb+ctrl-w+ to search, and search for ``\verb+quiet splash+''.
\item Change ``\verb+quiet splash+'' to ``\verb+quiet nosplash text+''.
\item Press \verb+ctrl-o+ to save, and \verb+ctrl-x+ to exit.
\item Type ``\verb+update-grub2+'' to apply the configuration change.
\item Type ``\verb+systemctl disable mdm+'' to turn off the GUI manager.
\item Type ``\verb+shutdown -r now+'' to reboot.
%
\item (The machine should boot per normal.)
\item If the machine has a black screen, press \verb+ctrl-alt-F6+ to get
to a text console.
\item Log in as ``\verb+root+'' with the password ``\verb+administrator+''.
\item Type ``\verb+ifconfig+'' to get network interface information. Look
for a field named ``\verb+HWaddr+''; this is the MAC address for a given
network interface. Write down (and doublecheck) the MAC address for the
ethernet jack (the device name will start with ``\verb+eno+'' or
``\verb+eth+'').
\item Plug the NeuroCam computer into one of the router's LAN ports.
\item Add the hardware address to the router's whitelist so that the
NeuroCam computer can see the network (per Chapter \ref{router}).
\item Wait 10 seconds, and then type ``\verb+ifconfig+'' again. When network
handshaking has finished, there will be an ``\verb+inet addr+'' field with
an IP address assigned. This address should be ``\verb+192.168.1.NN+'', for
some number ``\verb+NN+''.
\item Plug an internet cable into the router's WAN port so that the internet
is visible.
\par
\textbf{This is needed in order to update the operating system, but should
otherwise be disconnected.}
\item Type ``\verb+ping 8.8.8.8+'' to check internet connectivity. A response
of ``\verb+64 bytes from 8.8.8.8+'' means that the internet is visible.
\item Type ``\verb+mkdir /usb+'' to create a manual mount point for the USB
stick. This only needs to be done once.
\item Make sure no other USB sticks are in the machine, and insert a
NeuroCam update USB stick.
\item Type ``\verb+mount -t auto -o exec /dev/sdb1 /usb+'' to manually mount
the USB stick and to allow scripts to be run from the stick.
\par
\textbf{NOTE:} If a second solid--state drive is in the system (see below),
use ``\verb+/dev/sdc1+'' instead of ``\verb+/dev/sdb1+'' above.
\item Type ``\verb+/usb/neurocam-install/scripts/do-install.sh+'' to perform
first-time NeuroCam software installation. This will take a while.
\par
\textbf{NOTE:} This should skip most confirmation steps, but may still ask for
user input. Default settings should always be acceptable.
\item Once this has finished, type ``\verb+shutdown -r now+'' to reboot.
\item Remove the USB stick when the system reboots.
\item Disconnect the router from the internet by unplugging the WAN cable.
%
\end{itemize}

%
\subsection{Updating Linux and the NeuroCam Software}

Updating Linux may be done whenever desired. This normally isn't needed,
unless a NeuroCam software update indicates that it needs updated OS
packages as well.

\textbf{NOTE:} If the NeuroCam computer is ever exposed to the internet or
to any other external network, keeping Linux updated is a good idea, as this
will patch security holes that are discovered in its software.

Updating Linux Mint requires an internet connection. Updating the NeuroCam
software does not.

To update Linux Mint:
\begin{itemize}
%
\item (Turn on the machine and allow it to boot per normal.)
\item If the machine has a black screen, press \verb+ctrl-alt-F6+ to get
to a text console.
\item Log in as ``\verb+root+'' with the password ``\verb+administrator+''.
\item Plug the NeuroCam computer into one of the router's LAN ports.
\item Wait 10 seconds, and then type ``\verb+ifconfig+''. When network
handshaking has finished, there will be an ``\verb+inet addr+'' field with
an IP address assigned. This address should be ``\verb+192.168.1.NN+'', for
some number ``\verb+NN+''.
\item Plug an internet cable into the router's WAN port so that the internet
is visible.
\par
\textbf{This is needed in order to update the operating system, but should
otherwise be disconnected.}
\item Type ``\verb+ping 8.8.8.8+'' to check internet connectivity. A response
of ``\verb+64 bytes from 8.8.8.8+'' means that the internet is visible.
\item Type ``\verb+~/neurocam-scripts/do-mintupdate.sh+''. This may take a
while, depending on how many packages need to be updated.
\par
\textbf{NOTE:} This should skip most confirmation steps, but may still ask for
user input. Default settings should always be acceptable.
\item Once this has finished, type ``\verb+shutdown -r now+'' to reboot.
\item Disconnect the router from the internet by unplugging the WAN cable.
\end{itemize}

To update the NeuroCam software:
\begin{itemize}
%
\item (Turn on the machine and allow it to boot per normal.)
\item If the machine has a black screen, press \verb+ctrl-alt-F6+ to get
to a text console.
\item Log in as ``\verb+root+'' with the password ``\verb+administrator+''.
\item Make sure no other USB sticks are in the machine, and insert a
NeuroCam update USB stick.
\item Wait five seconds, then type ``\verb+mount /usb+''.
\item Type ``\verb+~/neurocam-scripts/do-update.sh+''.
\item Once this has finished, type ``\verb+shutdown -r now+'' to reboot.
\item Remove the USB stick when the system reboots.
%
\end{itemize}

%
\subsection{Logging In Over the Network}

When logging into a NeuroCam machine on--site, installing a monitor might not 
be practical. As long as a machine is available that is authorized to connect
to the NeuroCam network, logging in can be done remotely.

To log into the NeuroCam machine using a network connection:
\begin{itemize}
\item Connect to the NeuroCam system's wireless network.
\item Connect to the NeuroCam machine using the ``\verb+ssh+'' protocol with
username ``\verb+neurocam-admin+''. Under Linux or MacOS, this can be done
from a terminal window by typing ``\verb+ssh neurocam-admin@192.168.1.NN+'',
where ``\verb+NN+'' is from the IP address from the sticker on the NeuroCam 
machine. Under Windows, a ``terminal program'' such as ``\verb+PuTTY+'' may
be needed.
\item Enter the ``\verb+neurocam-admin+'' account's password when prompted.
\item Type ``\verb+su+'' (\textbf{not} ``\verb+sudo+'').
\item Enter the ``\verb+root+'' account's password when prompted.
\item Type ``\verb+cd ~+''
\item You are now logged in as ``\verb+root+'' and are in \verb+root+'s
home directory.
\end{itemize}

%
\subsection{Resetting Passwords}
\label{machine-password}

To reset a password for an account that you know the existing password for:
\begin{itemize}
\item Log in as that account.
\item Type ``\verb+passwd+''.
\item Enter the new password when prompted.
\end{itemize}

To reset the ``\verb+neurocam-admin+'' password when you \textit{can} log
in as ``\verb+root+'':
\begin{itemize}
\item Log in as ``\verb+root+''.
\item Type ``\verb+passwd neurocam-admin+'' to reset the account password
for ``\verb+neurocam-admin+''.
\item Enter the new password when prompted.
\end{itemize}

To reset the ``\verb+root+'' password when you \textit{can} log in as
``\verb+neurocam-admin+'':
\begin{itemize}
\item Log in as ``\verb+neurocam-admin+''.
\item Type ``\verb+sudo bash+'' to get a root shell. Enter the password
for the ``\verb+neurocam-admin+'' account as the \verb+sudo+ password.
\item Type ``\verb+passwd+''.
\item Enter the new password when prompted.
\item Type ``\verb+exit+'' to leave the root shell.
\end{itemize}

To reset the ``\verb+neurocam-admin+'' password when you \textit{cannot}
log into the NeuroCam machine at all, do the following:
\begin{itemize}
\item With the machine unpowered, plug in the Mint 18.1 USB stick.
\item Turn on the machine.
\item Hit F10 to enter the boot menu.
\item Select the USB stick from the boot devices, and boot.
\item (The machine should now show the Linux boot menu.)
\item From the Linux boot menu, pick ``start in compatibility mode''.
\item From the GUI, open a terminal window.
\item Type ``\verb+sudo bash+'' to get a root session.
\item Type ``\verb+mount -t auto /dev/sda1 /mnt+'' to mount the hard disk
in the ``\verb+/mnt+'' mount point.
\item Type ``\verb+chroot /mnt+'' to open a new shell that uses
``\verb+/mnt+'' as the root folder.
\item Type ``\verb+passwd neurocam-admin+'' to reset the account password
for ``\verb+neurocam-admin+''.
\item Enter the new password when prompted.
\item Type ``\verb+shutdown -r now+'' to reboot.
\item Remove the USB stick when the system reboots.
\end{itemize}

%
\subsection{Adding a Second Drive}

The instructions above configure a machine to use a single solid--state drive.
A second drive may be added, and given a single data partition; the two data
partitions (on the first and second drive) may then be configured as a single
larger \verb+RAID0+ drive.

\fixme{This hasn't been implemented, so no documentation for it.}

\fixme{Cover ``doing this before install'' and ``modifying a machine after
install'' separately.}

%
%
\section{Making New NeuroCam Install USB Sticks}
\label{machine-usb}

The NeuroCam install and update software can be added to any USB stick. This
does not interfere with existing data; the software is placed in a new
directory called ``\verb+neurocam-install+''.

To add the install and update software to an already-formatted USB stick:
\begin{itemize}
\item On a NeuroCam development machine, open a terminal window.
\item Navigate to the NeuroCam development directory.
\item Make sure no other USB sticks are in the machine, and insert a USB
stick to turn into a NeuroCam update USB stick.
\item Type ``\verb+install/scripts/make-installkey.sh+''.
\item Wait until the script has finished.
\item Type ``\verb+umount /media/neurocam-admin/(label)+'' to unmount the
USB stick for safe removal.
\par
This refers to Mint's automatic mount point for the USB stick, with 
``\verb+(label)+'' replaced with the stick's volume label (or serial number if
there is no volume label). You can use ``tab completion'' to avoid having to
type this: if only one USB stick is plugged in,
``\verb+/media/neurocam-admin/(tab)+'' will automatically expand to the
correct mount point name when the \verb+tab+ key is pressed.
\end{itemize}

%
%
\section{Making New Linux Mint USB Sticks}
\label{machine-usbmint}

The Linux Mint install software requires a dedicated USB stick. Adding the
Linux Mint installer destroys all other contents of the stick.

The version of Linux Mint used by the NeuroCam machines as of this writing
is 18.1.

To make a Linux Mint USB stick:
\begin{itemize}
\item On a Linux machine (such as a NeuroCam development machine), open
a browser and go to ``\verb+https://www.linuxmint.com+''.
\item Click on the ``Download'' tab.
\item Check the version number shown on the download page. If this does not
match the desired version, click on the ``All versions'' tab, and select the
desired version.
\item Select the 64-bit version with your desired desktop. NeuroCam
development was done using the ``Cinnamon'' desktop, but other desktops
should work.
\item Choose a mirror in the appropriate country to download the \verb+.iso+
image for your selected distribution. This may take some time to download.
Save this image and make note of its name and where you put it.
\item Click the terminal icon in the hotbar or start menu to get a terminal
window.
\item Type ``\verb+sudo apt-get install unetbootin+'' to make sure the
boot stick creation application is present. Enter your password when
prompted.
\item Type ``\verb+cat /proc/partitions+''. Insert the USB stick, close the
file browser popup (if any), then type ``\verb+cat /proc/partitions+'' again.
The newly-added lines indicate the device name of the USB stick (usually
``\verb+/dev/sdb+'' for the stick itself and ``\verb+/dev/sdb1+'' for the
data partition on it).
\item If desired, reformat the USB stick and set a meaningful volume label.
\par
To do this manually, ``eject'' (unmount) the USB stick, and type \\
``\verb+sudo mke2fs -j -m 0 -L (label) /dev/(partition device)+''. \\
Enter your password when prompted.
\item Type
``\verb+unetbootin method=diskimage isofile=(file) installtype=USB+ \\
\verb+targetdrive=/dev/(partition)+''.
\item Enter your password when prompted.
\item The UNetbootin dialog should already have the ``Diskimage'' method
selected, of type ``ISO'', with the filename filled in. Type should already
be ``USB Drive'', with target drive set to the partition name on the USB
stick. Verify this information, and click ``Ok''.
\item (UNetbootin will copy the install image to the USB drive and install a
boot loader.)
\item Click ``Exit'' to exit UNetbootin.
\item Type ``sync'' to commit all changes to disk.
\item Eject the USB drive, remove it, and then verify it by attempting to
boot a test machine using it.
\end{itemize}

%
% This is the end of the file.

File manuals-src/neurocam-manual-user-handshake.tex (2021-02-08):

% NeuroCam manual - Game Machine Handshaking
% Written by Christopher Thomas.
% Copyright (c) 2021 by Vanderbilt University. This work is released under
% the Creative Commons Attribution-ShareAlike 4.0 International License.

\chapter{Game Machine Handshaking}
\label{handshake}

The NeuroCam system queries machines on the local network to find content
providers. For the prototype system, the only network content provider is
the game machine.

The game machine should listen for UDP packets on port 8888. These will
be any of the following messages in plain text:
\begin{itemize}
\item ``\verb+looking for sources reply to port NNNN+''
\item ``\verb+talk to me on port NNNN+''
\item ``\verb+stop talking+''
\end{itemize}

The game machine may send any of the following responses:
\begin{itemize}
\item ``\verb+stream source at http://URL label XXXX+''
\item ``\verb+message source at HOST:PORT label XXXX+''
\item ``\verb+MSG (message text goes here)+''
\end{itemize}

The game machine will typically offer one video stream (the game video) and
one message source (which sends plain text timestamps for synchronization of
game events and NeuroCam data).

The video URL will generally be of the form
``\verb+http://(host IP):(port)/(file).mjpeg+''. Any valid URL should work,
as long as the file has the suffix ``\verb+mjpeg+'' and as long as the
host is given by IP address rather than hostname. This video stream will be
fetched by the NeuroCam and treated like any other camera feed.

Message sources must use IP addresses (not hostnames) as the host identifier.
These will be sent ``\verb+talk to me+'' and ``\verb+stop talking+''
messages, and when active are expected to send plain text UDP messages to
the NeuroCam machine. Messages are expected to begin with ``\verb+MSG +'',
with message content transcribed to the NeuroCam session log file. Message
source and NeuroCam timestamp information are also recorded in the log.

Multiple machines may respond to the broadcast query, and the same machine
may respond multiple times to one query. As long as the message and video
stream sources indicated by the responses are unique, they will all be
available to the NeuroCam system.

%
% This is the end of the file.

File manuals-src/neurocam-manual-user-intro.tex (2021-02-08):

% NeuroCam manual - Overview
% Written by Christopher Thomas.
% Copyright (c) 2021 by Vanderbilt University. This work is released under
% the Creative Commons Attribution-ShareAlike 4.0 International License.

\chapter{Overview}
\label{intro}

The NeuroCam system is a computer-controlled camera network that collects
footage of a subject interacting with a game (or other apparatus).
It was commissioned by the Attention Circuits Control Laboratory
(\verb+http://accl.psy.vanderbilt.edu/+)
to facilitate their experiments.

A system diagram is shown in Figure \ref{fig-system}, below:

\begin{figure}[h]
\begin{center}

\end{center}
\caption{System block diagram.}\label{fig-system}
\end{figure}

The NeuroCam system processes several types of data and events (described
in detail in later sections):

\begin{itemize}

\item It collects frame data (with timestamps) from several cameras.

\item It collects streamed video data from the game machine.

\item It accepts web connections from authorized computers for control and
monitoring.

\item It provides a ``monitoring'' feed to the control computer showing
all video streams.

\item It records ``marker'' events when interface buttons are clicked on
the monitoring web page.

\item It records digital (TTL) signals from external equipment.

\item It accepts TTL ``start'' and ``stop'' signals from external equipment.

\item It offers collected data for examination, download, and
post-processing via a web interface after experiments have completed.

\end{itemize}

% NOTE - We can't mbox verbatim commands, so manually add line breaks.
To get started, connect an authorized machine to the ``\verb+neurocam+''
network and point it to \linebreak
``\verb+http://192.168.1.+\textit{(value)}''
(the IP address given on the sticker on the NeuroCam machine).

%
% This is the end of the file.

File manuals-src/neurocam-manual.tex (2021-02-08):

% NeuroCam manual - Top level
% Written by Christopher Thomas.
% Copyright (c) 2021 by Vanderbilt University. This work is released under
% the Creative Commons Attribution-ShareAlike 4.0 International License.

\documentclass[letterpaper,11pt]{report}
\usepackage[letterpaper]{geometry}
\usepackage{graphicx}
\usepackage{verbatim}

\geometry{nohead,footskip=0.3in,margin=0.75in}

% Force my paragraph style, darnit.
\usepackage{indentfirst}
\setlength{\parskip}{\baselineskip}

% Custom macros.
\newcommand{\fixme}[1]{\textbf{FIXME: #1}}

% Document body.
\begin{document}

% Title page.

\pagestyle{empty}

\begin{center}
%
\vspace*{1.5in}
{\Huge NeuroCam System Manual} \\
{\footnotesize Written by Christopher Thomas -- \today.} \\
%
\vspace*{1in}

%
\vfill
{\footnotesize \input{boilerplate}}
%
\end{center}
%
\clearpage
%
\pagestyle{plain}
\pagenumbering{roman}
\setcounter{page}{1}
%
\tableofcontents
%
\clearpage
\pagestyle{plain}
\setcounter{page}{1}
\pagenumbering{arabic}
% NOTE - "\thispagestyle" is used for part and chapter beginning pages,
% and overrides \pagestyle.
% Redefine it to be harmless.
% NOTE - The canonical solution ("\pagenumbering{gobble}") resets the page
% counter whenever it's used.
\renewcommand{\thispagestyle}[1]{}

% Part 1: User guide.

\clearpage
\pagestyle{empty}
\part{Using the NeuroCam System}
\pagestyle{plain}

\input{neurocam-manual-user-intro}
\input{neurocam-manual-user-setup}
\input{neurocam-manual-user-gui}
\input{neurocam-manual-user-repo}
\input{neurocam-manual-user-handshake}

% Part 2: Maintenance guide.

\clearpage
\pagestyle{empty}
\part{Making More NeuroCam Systems}
\pagestyle{plain}

\input{neurocam-manual-maint-machine}
\input{neurocam-manual-maint-router}
\input{neurocam-manual-maint-gpio}
\input{neurocam-manual-maint-cameras}
% NOTE - c920 IR modifications have been split off to their own document.

% Part 3: Developer guide.

\clearpage
\pagestyle{empty}
\part{Modifying the NeuroCam Software}
\pagestyle{plain}

\input{neurocam-manual-dev-machine}
\input{neurocam-manual-dev-netcomm}
\input{neurocam-manual-dev-structs}
\input{neurocam-manual-dev-funcs}
\input{neurocam-manual-dev-progs}

\end{document}

%
% This is the end of the file.

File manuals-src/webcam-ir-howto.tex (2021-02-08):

% Webcam infrared HOWTO - Extracted from the NeuroCam manual.
% Written by Christopher Thomas.
% Copyright (c) 2021 by Vanderbilt University. This work is released under
% the Creative Commons Attribution-ShareAlike 4.0 International License.

\documentclass[letterpaper,11pt]{article}
\usepackage[letterpaper]{geometry}
\usepackage{graphicx}
\usepackage{verbatim}

\geometry{nohead,footskip=0.3in,margin=0.75in}

% Force my paragraph style, darnit.
\usepackage{indentfirst}
\setlength{\parskip}{\baselineskip}

% FIXME - Turn sections into subsections and chapters into sections.
\let\chapter=\section
\let\section=\subsection

% Document body.
\begin{document}

%
% Title and copyright notice.
%
\begin{center}
%
{\Huge Webcam IR Modification HOWTO} \\
\vspace*{0.5\baselineskip}
{\footnotesize Written by Christopher Thomas. \input{boilerplate}}
%
\end{center}

%
% Camera-specific instructions.
%
\input{neurocam-manual-aux-c920}

\end{document}

%
% This is the end of the file.

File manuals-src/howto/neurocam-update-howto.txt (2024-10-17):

This summarizes how to update the NeuroCam software. The full description is
in the NeuroCam manual, which is on TEBA in "Procedures and SOPs/Neurocam".
As of September 2021, the update method is on page 22.

Short version:

* Log into the NeuroCam, as the "root" account. There are two ways to do this:
  - The first is to plug a keyboard and monitor into the NeuroCam, press
    ctrl-alt-F6 to get a text console, and then log in as "root" with the
    password in the manual.
  - The second is to use a tablet or other machine that has a wireless
    connection to the NeuroCam. Use SSH to log in as the "neurocam-admin"
    user ("ssh neurocam-admin@192.168.1.xxx"), with the normal NeuroCam
    password, then type "su" to become root (it'll ask you for the root
    password at that point).
* Once you're logged in as root, plug the NeuroCam update stick into the
  NeuroCam, wait a slow count of 10, then type
  "~/neurocam-scripts/do-update.sh".
* When it's finished, type "shutdown -r now" to reboot, and remove the USB
  stick when it boots.

You can check that the NeuroCam has been updated by logging into the web
interface and looking for the version number.

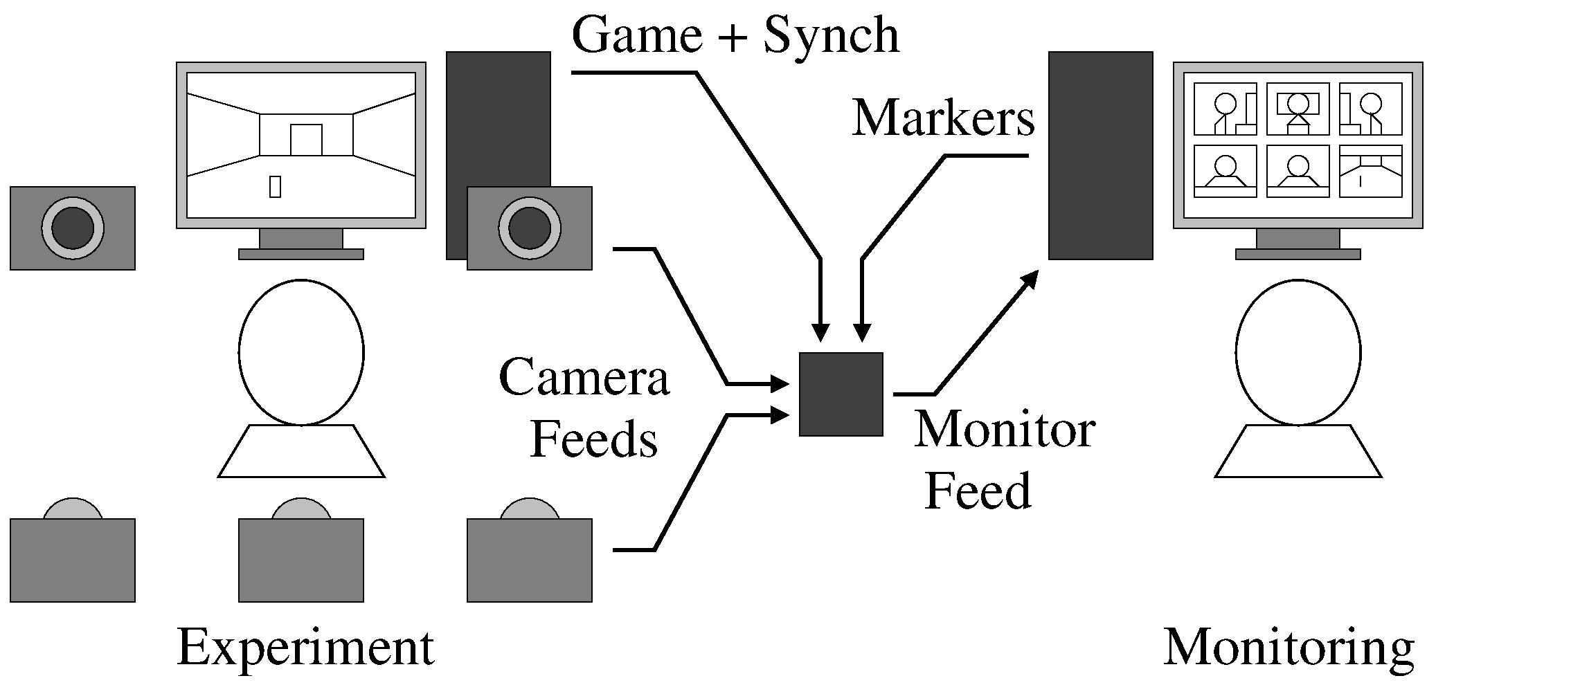
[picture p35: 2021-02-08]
manuals-src/figs/system-ext.png

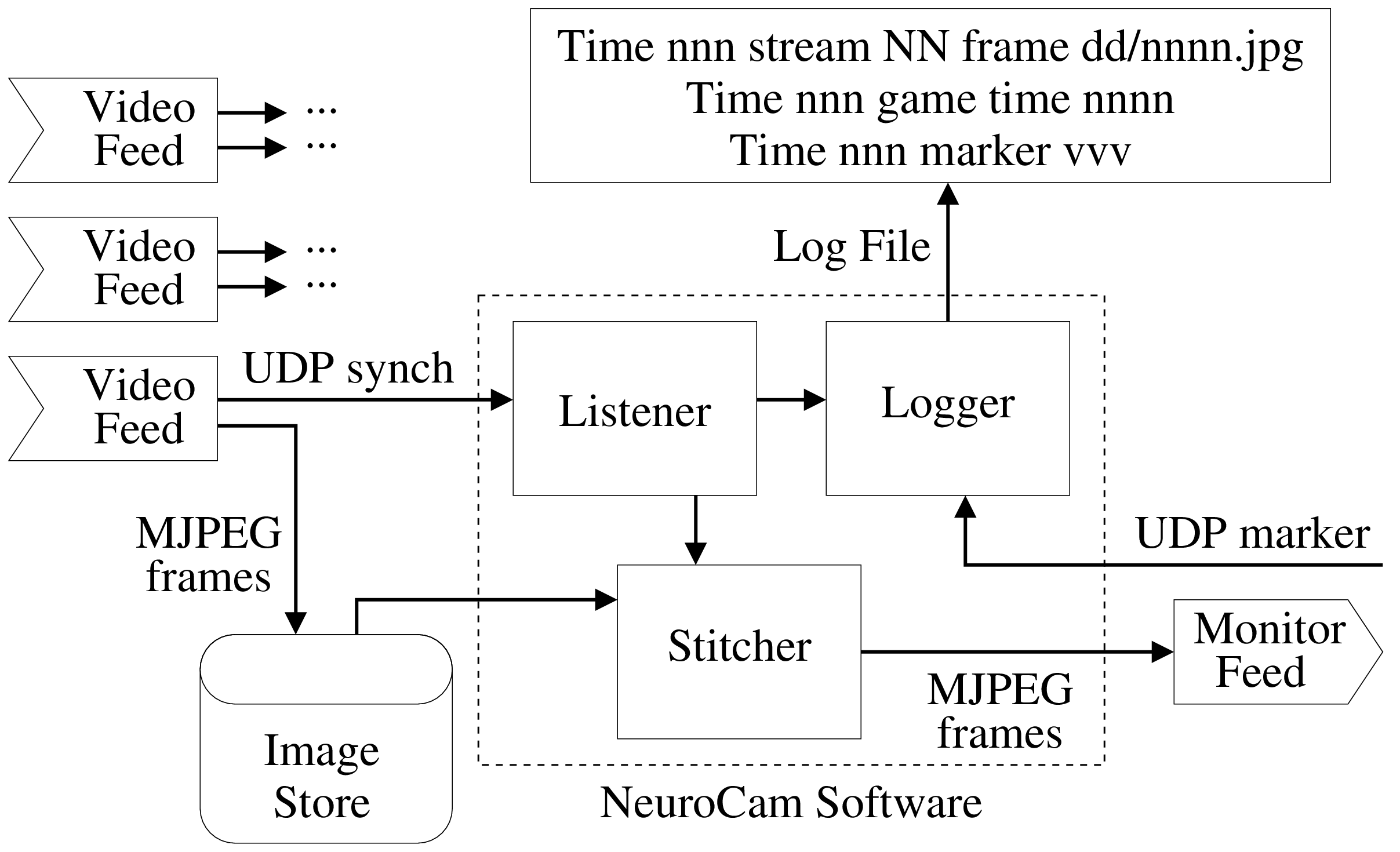
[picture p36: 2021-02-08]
manuals-src/figs/system-int.png

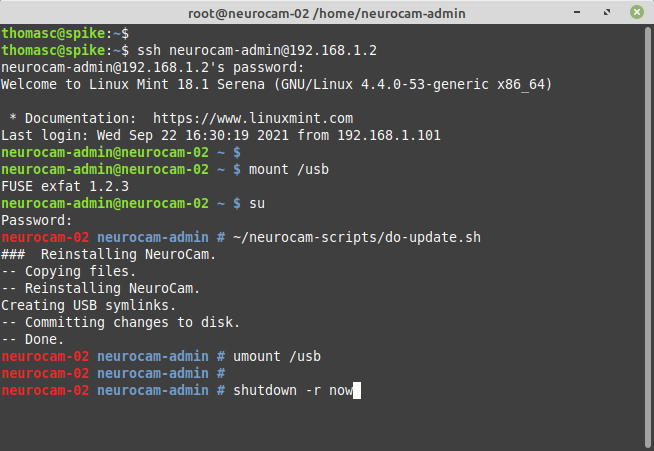
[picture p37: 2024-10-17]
manuals-src/pics-update/orig-20210922/neurocam-update-with-ssh.png

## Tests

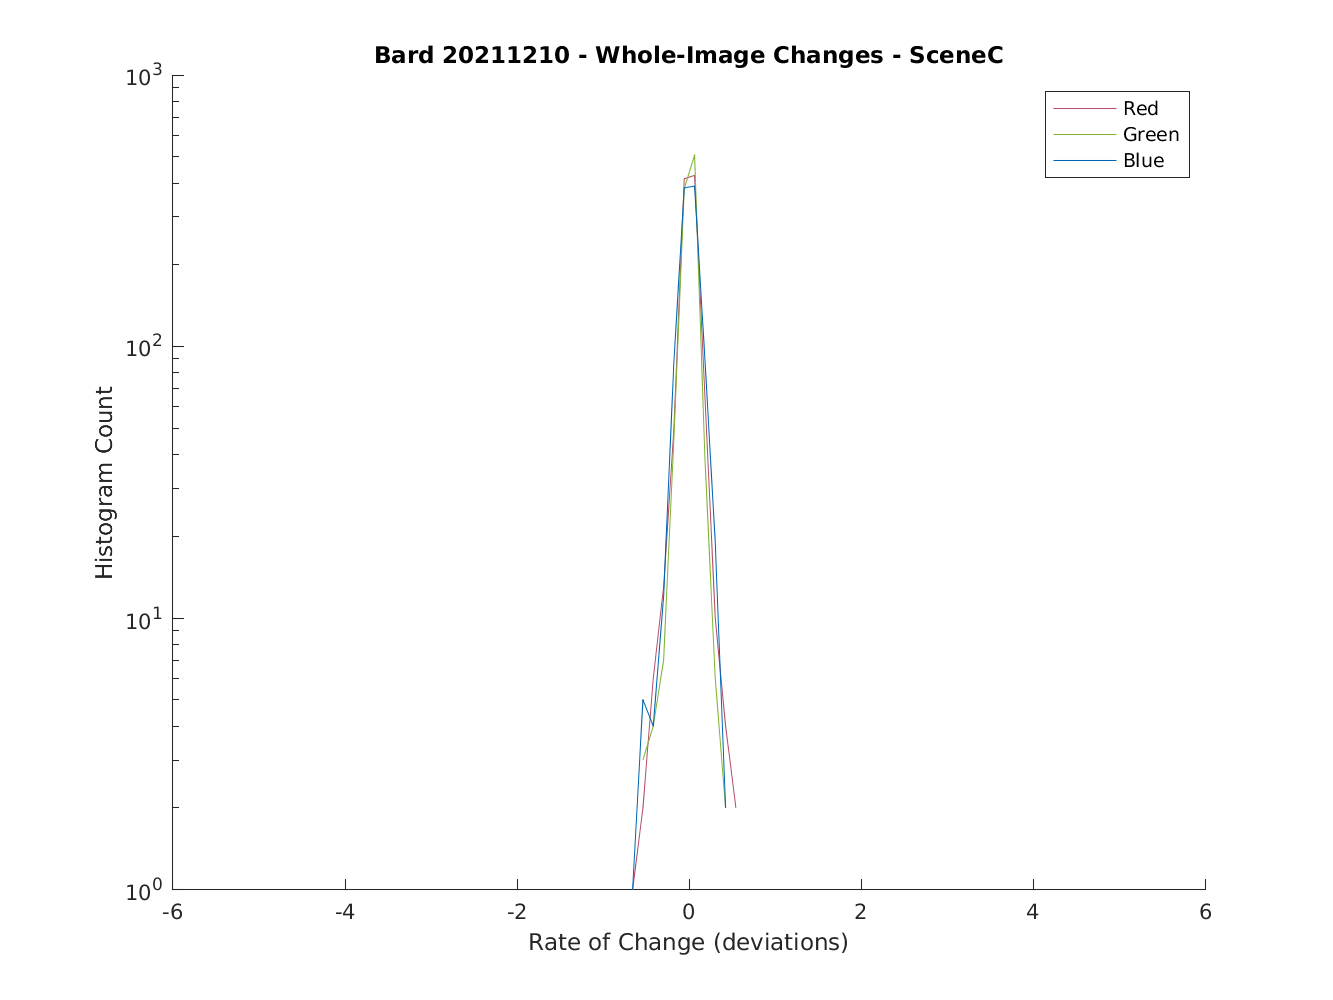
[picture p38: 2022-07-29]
matlab/milestones/20220728-test/plots/bard-SceneC-average.png

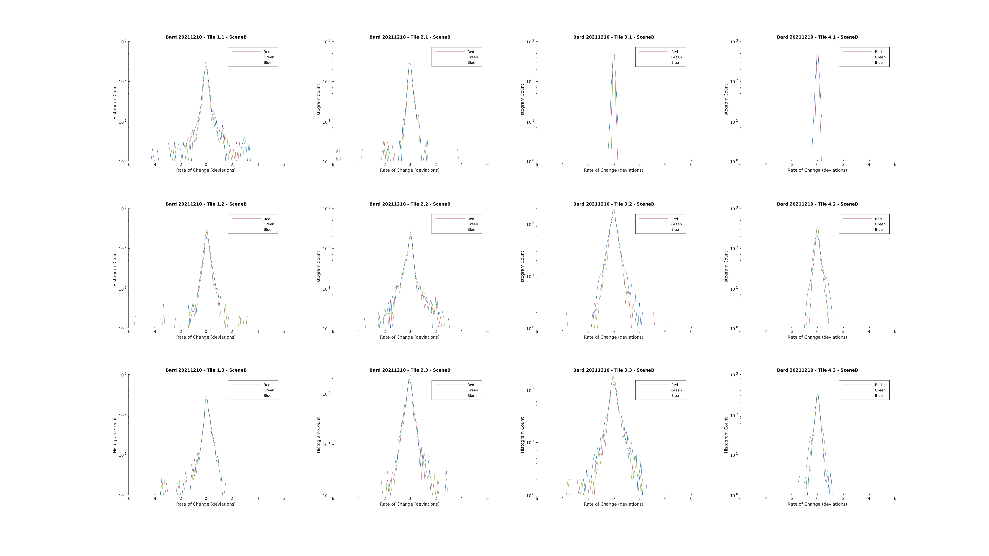
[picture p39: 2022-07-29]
matlab/milestones/20220728-test/plots/bard-SceneB-tiles.png

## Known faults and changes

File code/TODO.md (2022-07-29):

# Attention Circuits Control Laboratory - NeuroCam daemon and client scripts
# Change log, bug list, and feature request list.
Written by Christopher Thomas.

## Bugs and feature requests:

* "avconv" doesn't exist on Mint 20. Auto-detect "avconv" vs "ffmpeg".

* Sometimes the video feed is a broken link (perhaps due to using an old
folder name, due to starting a new feed too quickly?).

* Make "NCAM_QueryCameraParamsRaw" and use it in libcam.pl.

* Modify GrabFrame and TestCapture to set camera state while running.

* Make a "RunCamera" function (with UDP update and fixed frame count options).

* Make a "ConfigureCamera" function to call before and after RunCamera.

* Give the NeuroCam a proper task queue.

* Make a headless processing client for the NeuroCam so that post-processing
can be done on workstations/servers.

* Restrict exposure settings for the Logitech c930 to allowed values.
Values that aren't "magic" values are immediately reset by the camera.

* First-time access with no cameras or game stream present gives a broken
image icon for the preview. "Refresh preview" fixes it.

* Pressing "cancel" when building a tarball removes post-processed data.

* Compositing is very time-consuming.

*  Resizing the monitor stream is somewhat time-consuming.

*  Some operations have no progress indicator. [break out into specific ops]

* Add a log file for post-processing.

* Add a log file for debugging. In /tmp is fine. (FIXME: no, that gets wiped)

* Add support for ethernet cameras.

* Look into gstreamer instead of ffmpeg for camera capture.

* Generate a warning when the hard drive fills up (or is low on space).

* Allow batch-copy, batch-move, and batch-delete of multiple files.
  ** This will be needed when we have more kiosks, to avoid babysitting.

* Allow monitoring without recording (for when the disk is full).

* Make the install script put the repository directory on /data but keep the
CGI/config directory local, so that filling the data disk doesn't lose 
configuration information.

* Adjust UI buttons to be usable on an iPad (and avoid "oops" scenarios).

* Allow per-camera "ignore synch LED", for situations where we only have LEDs
on some of the cameras.

* Have the NeuroCam check disk health via "smartctl" and report problems.

* Have the NeuroCam check temperature via
  "cat /sys/class/thermal/*zone/t[ye]*" and report problems.

* Update the post-processing command-line tools' help page to show that it
needs a reporting port when doing time alignment.

* When the system updates packages, permissions on "shutdown" can be reset.
Run "chmod u+s /sbin/shutdown" from our update script.

* The NeuroCam script allows all combinations of resolution and frame rate,
but some cameras (like the "ELP" ones from 2019) need specific combinations.
If the wrong combination is chosen, the camera vanishes from the device list.
Have the script sanity-check requested combinations against detected modes.

* Some cameras (like the Nexigo N980P) don't have exposure control. Make the
NeuroCam script tolerate missing controls.

* Make the NeuroCam save a list of available controls and check against the
list when updating camera settings.

* Make the NeuroCam adjust gain rather than exposure by default.

## Low priority bugs and feature requests:

* Fix all of the speed problems in the NeuroCam code. This will involve
writing various daemons in C (capturing and compositing, at minimum).

* Make the NeuroCam work with ethernet cameras (in addition to USB cameras).

* Make UDP commands to set and query camera configuration.

* Modify the web GUI to allow setting camera configuration while cameras are
running.

* Modify the web GUI to allow setting additional camera parameters besides
exposure.

## Abbreviated changelog (most recent changes first):

* 16 Sept 2021 --
Explicitly added "." to the library search path (no longer there by default).

* 14 Sept 2021 --
Changed video transcoding bit rate to 10 Mbit (from 1 Mbit). 1080p was
looking terrible at the old rate.

* 15 Feb 2021 --
Added vendor-specific metadata. Modified daemon capture code to set camera
configuration while the camera is running (as the c930 resets itself when
starting). Adjusted c930 default gain.

* 11 July 2018 --
_Metadata for deleted folders only goes away after "recalc sizes"._
Fixed; ghost entries are now marked as stale.

* 11 July 2018 --
_Deleting a USB folder (tarball) hangs._
Fixed.

* 11 July 2018 --
_USB tarballs have bad metadata (timestamp of 1 Jan 1970)._
Fixed.

* 03 July 2018 --
_Metadata for deleted folders remains present._
Fixed (I think).

* 03 July 2018 --
_ExFAT grinds to a halt with large numbers of files._
Modified CGI logic so that USB folders are stored as .tar archives.

* 27 June 2018 --
_EFI drives mount the EFI partition rather than the main partition._
Overhauled external drive routines to consider both cases. Added a second
mountpoint and symlink.

* 26 June 2018 --
_Shutdown page never renders._
Fixed by launching a shutdown script as a daemon, so that the
CGI script can terminate before the shutdown happens.

* 26 June 2018 --
_Software restart and machine shutdown are confusingly placed._
Buttons the user should be careful with are now red. Buttons
that change mode or are otherwise important are now green. Most have no
colour.

* 26 June 2018 --
_Installer doesn't set /data to web directory._
Fixed. Also made safe for multiple install invocations.

* 13 May 2018 --
_List of frames is truncated due to "ls *.jpg"._
Fixed by changing "ls *.jpg" to "ls|grep jpg" in libpost.pl.

This is the end of the file.

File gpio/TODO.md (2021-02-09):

# Attention Circuits Control Laboratory - NeuroCam "Blink Box" GPIO device
# Change log, bug list, and feature request list.
Written by Christopher Thomas.

## Bugs and feature requests:

## Low priority bugs and feature requests:

* Port the GPIO device's code to use the "NeurAVR" application framework.

* Port the GPIO device's hardware to use the to-be-named standard project
PCBs.

## Abbreviated changelog (most recent changes first):

* 09 Feb 2021 --
Initial changelog document.

This is the end of the file.

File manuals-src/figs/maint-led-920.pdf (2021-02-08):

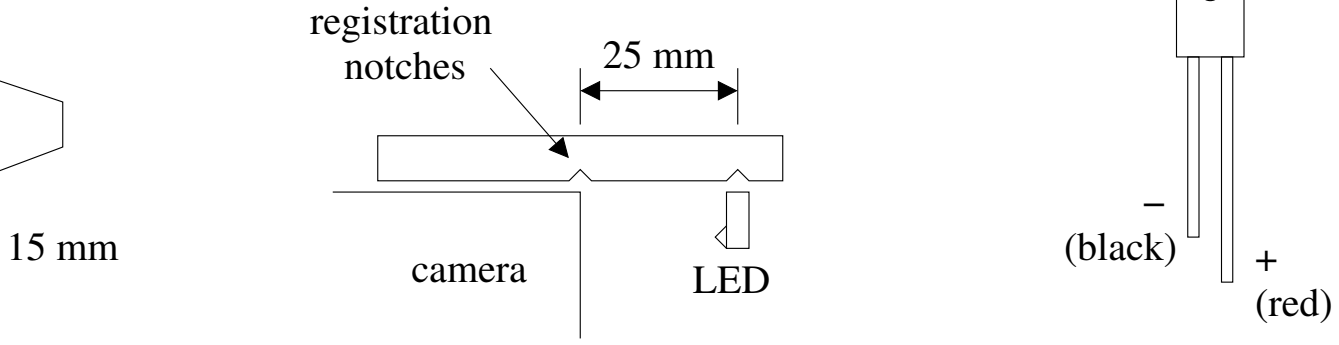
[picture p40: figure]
− (black); (red); camera; LED; registration notches

centreline

camera

Top View | Side View | LED Detail

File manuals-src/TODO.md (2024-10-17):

# Attention Circuits Control Laboratory - NeuroCam manual
# Change log, bug list, and feature request list.
Written by Christopher Thomas.

## Bugs and feature requests:

* "`structs`" reference undefined for "guide" target (it refers to a "dev"
chapter).

* "`c920`" reference undefined for "manual" target (content was moved to a
dedicated document).

## Low priority bugs and feature requests:

* Update with revised screenshots (GUI tweaked a while back).

* Add a cabling diagram to help non-technical people set the system up.

## Abbreviated changelog (most recent changes first):

* 08 Feb 2021 --
Cleaned up photo handling and rebuilds.

This is the end of the file.

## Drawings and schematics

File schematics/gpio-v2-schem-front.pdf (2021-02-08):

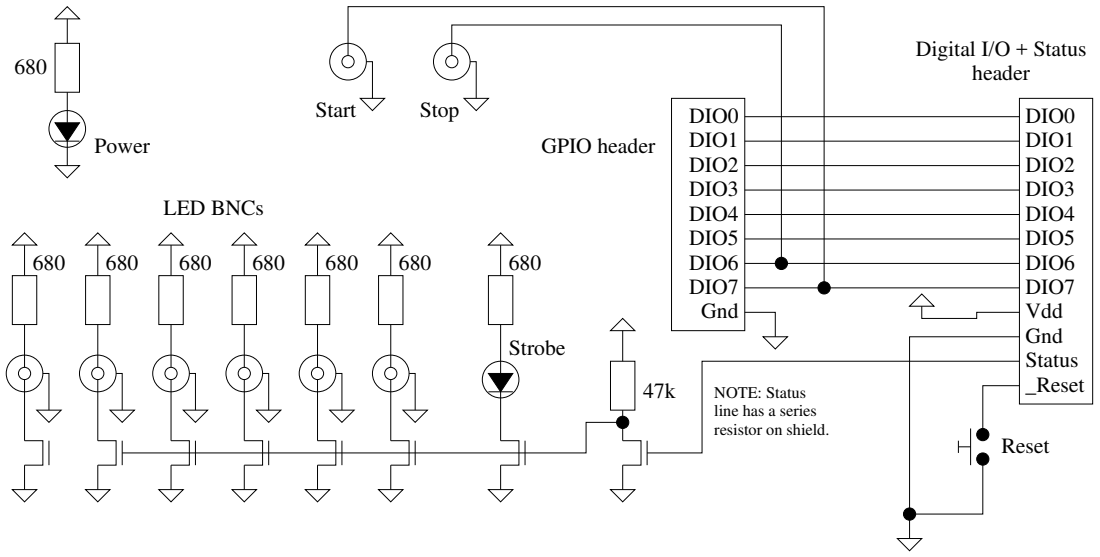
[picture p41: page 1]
DIO2; DIO1; DIO0; DIO3 DIO4 DIO5 DIO6 DIO7 Vdd Gnd Status _Reset; DIO0 DIO1 DIO2 DIO3 DIO4 DIO5 DIO6 DIO7 Gnd; Strobe; Power; GPIO header; Digital I/O + Status header; Start; Stop; Reset; LED BNCs

NOTE: Status
line has a series
resistor on shield.

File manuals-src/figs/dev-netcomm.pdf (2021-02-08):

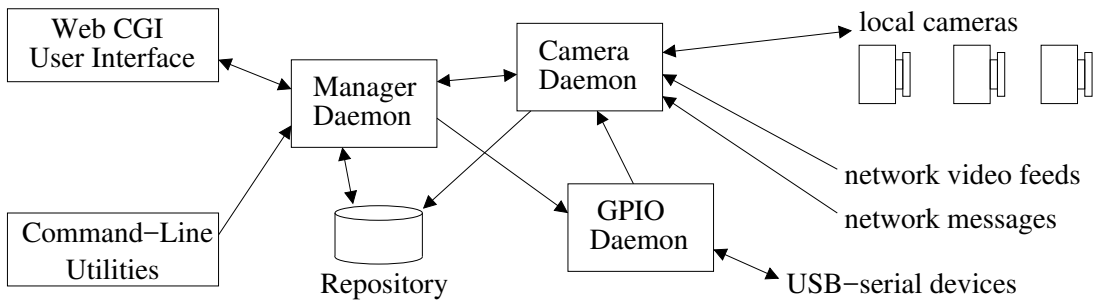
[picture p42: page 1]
Camera Daemon; GPIO Daemon; Web CGI User Interface; Command−Line Utilities; Manager Daemon; local cameras; Repository; USB−serial devices

network video feeds
network messages

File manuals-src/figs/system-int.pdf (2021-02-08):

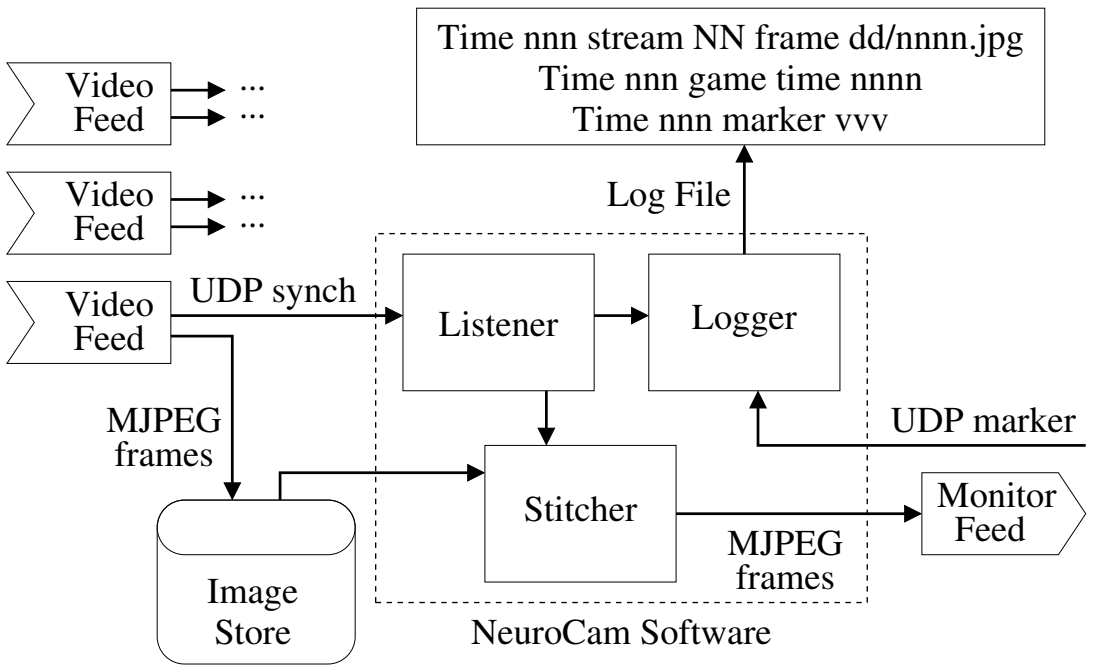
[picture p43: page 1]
Feed; Video; Store; Image; Monitor Feed; Log File; UDP synch; MJPEG frames; Listener; Stitcher; Logger; UDP marker; NeuroCam Software

Time nnn stream NN frame dd/nnnn.jpg

Time nnn game time nnnn
Time nnn marker vvv

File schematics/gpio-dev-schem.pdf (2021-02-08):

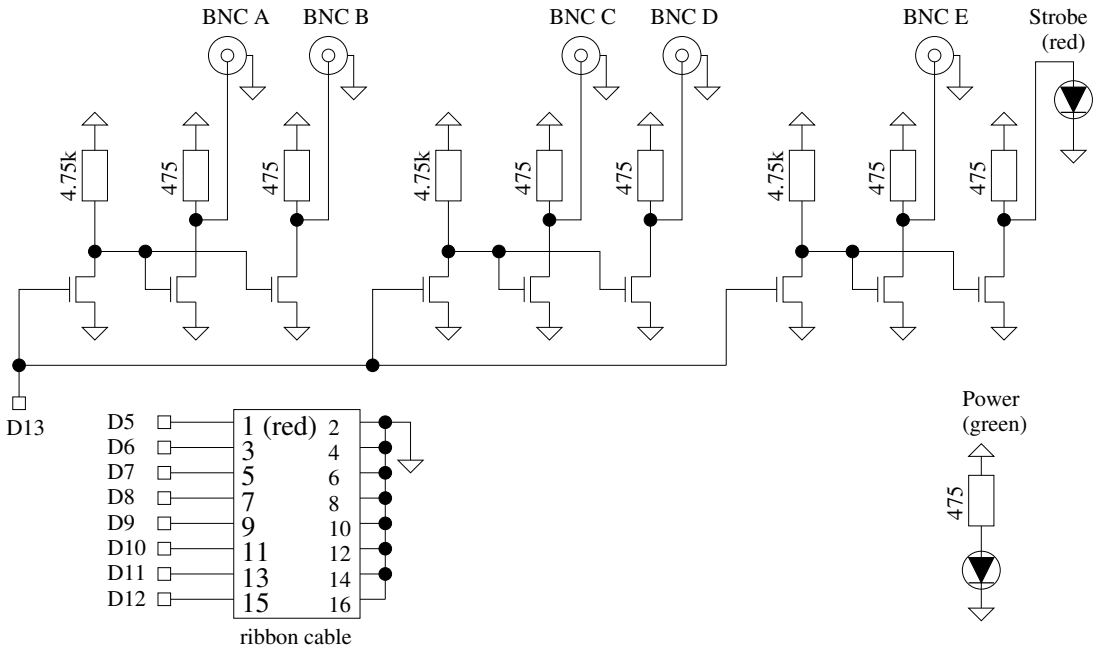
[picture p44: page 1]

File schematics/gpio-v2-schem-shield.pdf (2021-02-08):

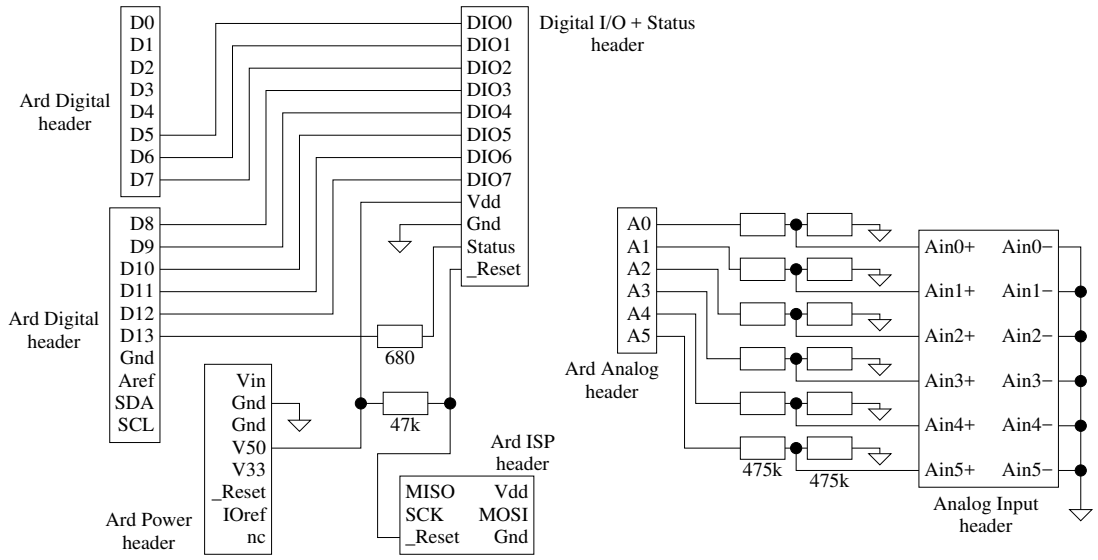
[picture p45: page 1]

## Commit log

2021-02-08 Added manuals. Added mechanical drawings and schematic drawings.
    [gpio-v2-back-inches.dxf, gpio-v2-back.dxf]
2021-02-09 Added GPIO firmware, PCB files, and header documentation.
    [gp2-led-gpio-stat.bottom.gbr, gp2-led-gpio-stat.bottommask.gbr, gp2-led-gpio-stat.bottompaste.gbr, gp2-led-gpio-stat.bottomsilk.gbr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]
2021-02-09 Moved GPIO material to its own folder. Added GPIO changelog.
    [gp2-led-gpio-stat.bottom.gbr, gp2-led-gpio-stat.bottommask.gbr, gp2-led-gpio-stat.bottompaste.gbr, gp2-led-gpio-stat.bottomsilk.gbr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]
2021-02-10 Added camera and computer part number notes from the 2020 search.
2021-02-15 Added device-specific metadata support. Added device-specific settings for Logitech c930e. Added code to apply camera settings during filming in addition to prior to filming.
2021-07-29 Documented low-level camera commands wrapped by the NeuroCam. Added feature requests regarding missing controls.
2024-10-17 Added camera probe notes.
